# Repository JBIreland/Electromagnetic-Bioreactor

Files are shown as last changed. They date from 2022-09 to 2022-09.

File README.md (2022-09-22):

# Electromagnetic-Bioreactor

The electromagnet enclosure was designed to be a safe and non-invasive method of modulating cellular substrate stiffness to induce biomimetic mechanical stimulation to matured and differentiating cardiomyocytes. This bioreactor is complimentary to the iron nanoparticle infused hydrogels developed in previously published works (1). Each of the electromagnets (APW Company, EM137-24-222) has a holding capacity of 20kg when 24V 0.2Amps is applied. The displacement of nanoparticles within the hydrogels is accomplished by modulation of the electromagnetic fields from 0 to 100% field strength, and the nature of an electronically controlled magnetic system provides precision application of the electromagnetic field. This enables tuning of differences observed in contraction profiles between immature and mature or healthy and diseased cardiomyocytes to be applied to the substrate of cells in culture that could potentially influence preconditioning or chamber specification of differentiating stem cell derived cardiomyocytes.

Physical design of the electromagnetic bioreactor
The layout of the electrical components for this bioreactor are displayed in the attached images. The key components of the system are the Digilent Analog Discovery 2 (Digilent, 410-321) and the OPA541 operational amplifier power module. The Digilent Analog Discovery 2 is a USB controlled oscilloscope, logic analyser, and variable power supply. It can be used straight out the box without modification and is controlled via computer software UI called Waveforms. The OPA541 operational amplifier power module is a commercial plastic control board (PCB) that can be purchased from several vendors including Amazon AU. It is designed to reliably amplify complex audio signals through a two phased amplification with an OPA445 followed by a larger OPA541. This design makes it uniquely capable for our application of amplifying complex contraction profiles but requires modifications to improve its reliability and total gain (modifications described in the attached images). Initially the OPA445 (Digi-Key, OPA445AU-ND) and OPA541 (Digi-Key, OPA541AP-ND) that are provided on the purchased power module are low quality and are replaced with better versions of these components from Texas Instruments. Secondly the gain amplification on the power module board is insufficient so 4 SMD resistors are exchanged for different resistance to control a gain amplification of 2 over the OPA445 and a gain amplification of 5 over the OPA541 which provides a total gain amplification of 10 (2x5). Finally, the incoming voltage to the power module board to drive the electromagnets is close to the operational threshold of the input capacitors. It is therefore wise to increase the capacitors operating voltage from 50V to 63V (Digi-Key, P123408-ND) to accommodate the electrical load. The Digilent Analog Discovery 2 and OPA541 operational amplifier power module components together can produce a customised wavefunction that represents the contraction profile of cardiomyocytes, and the amplification of that signal to drive 6 independent electromagnets. Each of the electromagnets (APW Company, EM137-24-222) has a holding capacity of 20kg when 24V 0.2Amps is applied. The operating temperature of the OPA541 operational amplifier power module can reach temperatures exceeding 100oC and thus required the design of a temperature-controlled air-cooling system (displayed in appendix 6). The air-cooling system uses a negative temperature coefficient (NTC) 10K Ohm thermistor (Jaycar, RN3440) that increases fan speed sequentially as temperature increases. The NTC works at a maximum resistance of 10K Ohms when its temperature is at 25oC and its resistance goes down as it gets hotter. The microcontroller used to operate the thermistor and fan speed is an Arduino mega 2560 Rev3 (Arduino, A000067). This type of microcontroller requires customised control software to be uploaded onto it which was created and uploaded using the Arduino IDE 2.0.0. The Arduino provides a 5V power output and reads the returning voltage on pin A0 over a voltage divider network using the 10K Ohm thermistor and a static 10K Ohm resistor. The equation we use to find the output voltage is described in the equation below 

V_out=  R_2/(R_1+R_2 )   x  V_in

Where V_out is the voltage read on Pin A0 of the Arduino microcontroller, R_2 is the static 10K Ohm resistor, R_1 is the NTC thermistor, and V_in is the 5V output voltage from the Arduino microcontroller that’s passed through the voltage divider network. As the temperature of the NTC thermistor increases its resistance decreases and an increased voltage is returned to the Arduino mega. The fan we are using is a 2 wire 24v brushless DC motor fan (Jaycar, X2542). The Arduino isn’t powerful enough to control the fan speed, so we modulate the amount of voltage the fan receives with a 2N7000 N-Channel field effect transistor (JayCar, ZT2400). The electrical schematic for this system is provided in the attached images.
The electromagnets themselves can exceed temperatures of 42oC which would create a hostile environment for cell culture growth and thus we engineered a water-cooling system for the electromagnets. This works using a water-cooling system designed for a home desktop computer and is modified to incorporate our own design of water flow valve and copper coils used for cooling the 540/550 brush motors of RC boats. The water-cooling systems schematic is shown in the attached images and all parts used in the construction of the electromagnetic bioreactor are listed in the parts list.

Operation of the electromagnetic bioreactor
The operation of the electromagnets is operated via the Waveforms software that controls the Digilent Analog Discovery 2. Upon opening he software we select program 4 with Scope of 2x215, Wavegen of 2x256, logic of 16x16, and pattern of 16x16. Selecting this program allows more of the distributed voltage inside the Digilent Analog Discovery 2 to be supplied to the wavegen function as this is what we will use most heavily. Using the protocol panel on the left of the welcome screen we select scope, wavegen, and supplies. In the supplies tab we set both the positive and negative voltage to 5V which provides the Arduino mega 2560 with 5V and 200 mA. This power supply allows the Arduino to run the thermistor regulated cooling fan next to the OPA541 operational amplifier. On the scope panel we set the base time to 2s/division and set the range for both scope channels to 5V. This provides a scope field from +25 to -25V that’s 20seconds long. Consulting the electromagnetic bioreactor schematic in Appendix 6 you can see channel 1 of the scope is connected to the output wavegen before it enters the OPA541 power module and channel 2 is connected to the output of the OPA541 power module. These settings allow for the visualisation of the wave function both before and after it’s been amplified and helps determine the efficiency of the OPA541 power module. In the wavegen tab we control the wave function that’s been generated by the Digilent Analog Discovery 2 that will be delivered to the electromagnets to manipulate the cells substrate. For testing we used a sine wave with a 1Hz frequency, an amplitude of 2.4V and offset of 0V, a symmetry of 50% and a phase of 0o. These settings are controlled from the “simple” panel in the wavegen tab. By switching to the “custom” panel in the wavegen tab we are presented with a panel with a multitude of options for designing a waveform. By selecting “File” we can upload a file that’s been normalized from 0 to 100% for the contraction profile of cardiomyocytes we have previously measured in the lab. Once the file has been uploaded, the contraction profile is present in the wavegen graph. We now click on run in the wavegen, scope, and supplies tabs and turn on the two bench power supplies supplying the input voltage to the OPA541 power module. We can now see in the scope window that the 2.4V sign wave being produced from the wavegen tab is displaying as two sign waves on the scope tab. The initial wavegen with an amplitude of 2.4V from channel 1 and a second wavegen with an amplitude of 24v from channel 2. We can then save these settings so we don’t need to reconfigure the waveforms software every time we run an experiment and we can run these wavegen programs continuously. 

Reference

1. Islam MS, Molley TG, Ireland J, Kruzic JJ, Kilian KA. Magnetic Nanocomposite Hydrogels for Directing Myofibroblast Activity in Adipose‐Derived Stem Cells. Adv NanoBio Res. 2021 Apr;1(4):2000072.

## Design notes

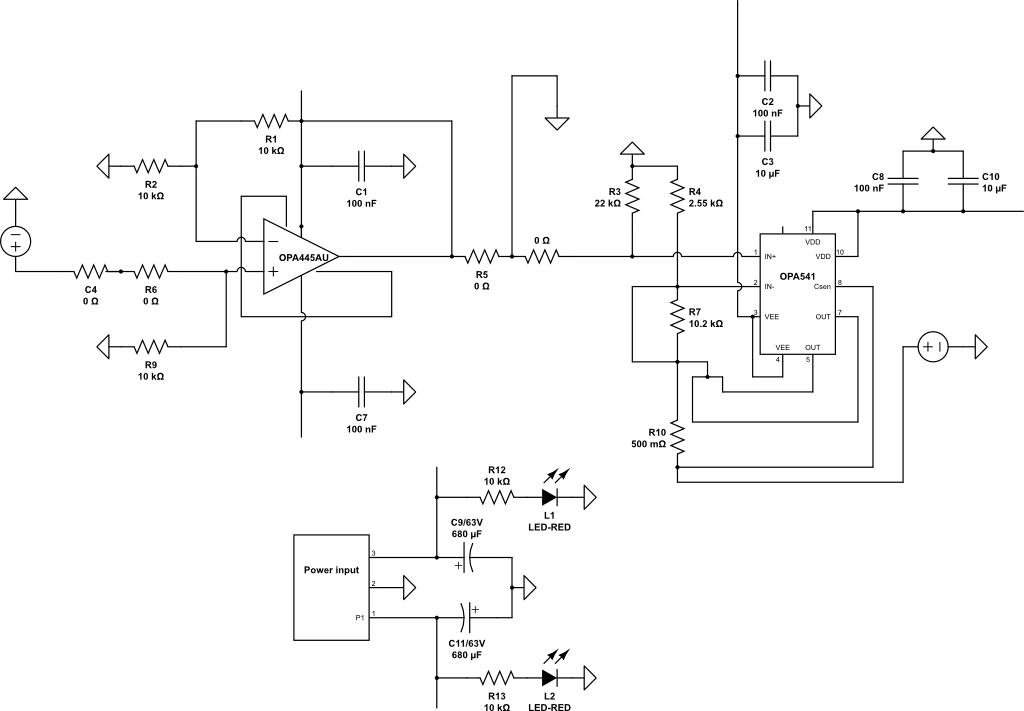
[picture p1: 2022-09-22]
OPA541 modification/OPA541 Power Module modified-schematic.png

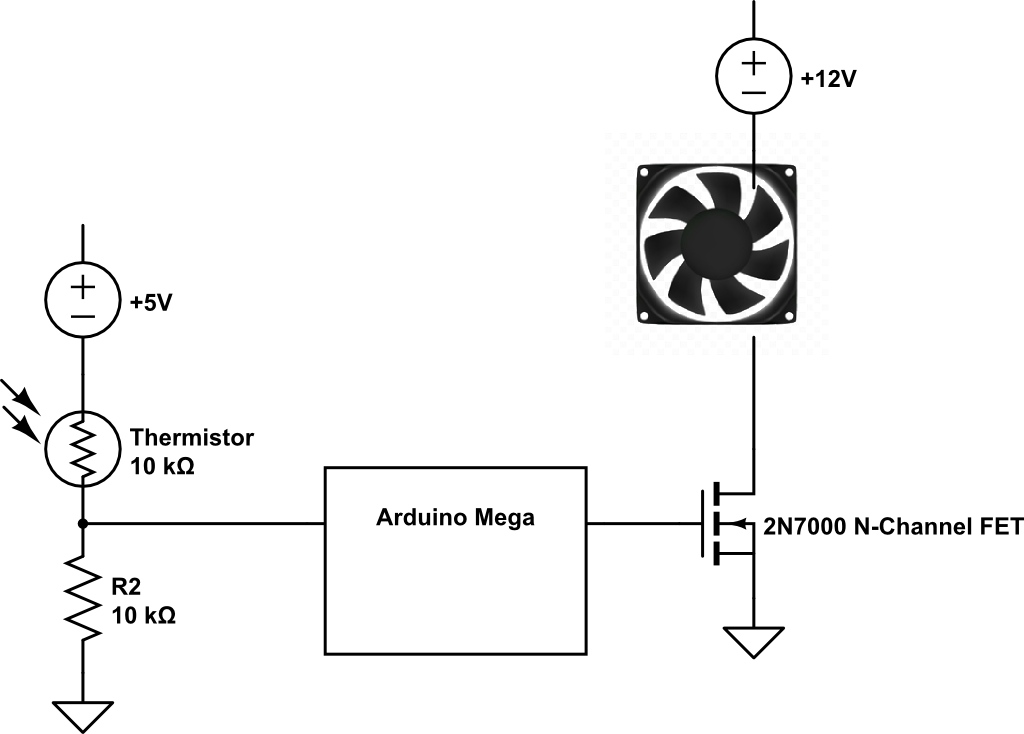
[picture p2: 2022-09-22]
fan_Control/fan-control-thermistor.png

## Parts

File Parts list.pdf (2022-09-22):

Parts list

Quantity | Part | Product Code | Company
6 | Electromagnets | EM137-24-222 | APW Company
| Copper Board | HP9558 | Jaycar
8 | 2 Way PCB Mount Screw Terminals 5mm Pitch | HM3172 | Jaycar
2 | 2 Pole PC Mount Pluggable Header -5.08mm - Vertical | HM3112 | Jaycar
2 | 2 Pole PC Mount Pluggable Header -5.08mm - Horizontal | HM3102 | Jaycar
4 | 2 Pole PC Mount Pluggable Terminal Block Socket - 5.08mm | HM3122 | Jaycar
1x20pack | Crimp Ferrule White 0.75mm² | PT4433 | Jaycar
1x 20pack | Crimp Ferrule Red Terminal Pack | PT4533 | Jaycar
1 pack | Breadboard Jumper wires | PB8850 | Jaycar
1 pack of 40 | 150mm Socket to Socket Jumper Leads | WC6026 | Jaycar
1 pack of 40 | 150mm Plug to Plug Jumper leads | WC6024
1 pack of 40 | 150mm Plug to Socket Jumper Leads | WC6028 | Jaycar
1 | OPA541 Module Power Amplifier Audio Amplifier | | Amazon AU
1 | Operational Amplifier OPA445 | OPA445AU-ND | Digi-Key
1 | Operational Amplifier OPA541 | OPA541AP-ND | Digi-Key
1 | 2.55K OHM SMD Resistor | P2.55KDACT-ND | Digi-Key
1 | 10.2K OHM SMD Resistor | P10.2KDACT-ND | Digi-Key
1 | 10K OHM SMD Resistor | P10KDACT-ND | Digi-Key
2 | 0 OHM SMD Resistor | P0.0KDACT-ND | Digi-Key
1 | 10K Resistor | | Elegoo
2 | Capacitors Cap Alum 68UF 20% 63V THRU HOLE | P123408-ND | Digi-Key
1 | 80mm 24VDC 2 wire Brushless Fan Motor | X2542 | Jaycar
1 | 80mm Plastic Fan Guard | YX2552 | Jaycar
1 | Arduino Mega 2560 Rev3 | A000067 | Arduino

1 | 10kΩ Epoxy Dip NTC Thermistor | RN3440 | Jaycar
1 | 2N7000 N-Channel FET | ZT2400 | Jaycar
1 | Analog Discovery 2: 100MS/s USB Oscilloscope, Logic Analyzer and Variable Power Supply | 410-321 | Digilent
1 roll | Narva 3mm x 10m 10Amp Red/Black Twin core power cable | 0047792 | Bunnings
2 | 30V 10A DC Power Supply | 72-2925 | Element14
1 | 3 Way Red WAGO PUSH WIRE Connector | HM3233 | Jaycar
1 | Breadboard | PB8815 | Jaycar
1 | 24V DC 1.25A Power Supply | MP3494 | Jaycar
1 | 5V DC 3A Slim Power Supply | MP3480 | Jaycar
1 | 12V DC 400mA Ultra-Slim Power Supply | MP3147 | Jaycar
1 | 3-12V DC 27W Power Supply | MP3316 | Jaycar
1 | Plastic Storage Container 10L Rectangular | 881880 | Sistema
1 | 900x600x5mm Clear Acyrlic Sheet | 1010490 | Bunnings
1 | Dark Grey Enclosure with Mounting Flange - 171(W) x 121(D) x 55(H)mm | HB6125 | Jaycar
1 | 3D Printed Bioreactor Cooling Valve | | Printed in house in Polycarbonate
1 | Kinetic O Ring Assorted Kit | 4920305 | Bunnings
1 | Pacific RL120 Radiator | CL-W011-AL00BL-A | Thermaltake
1 | 120mm PWM Curve Fan | CL-W069-CA00BL-A | Thermaltake
1 | Pacific PR22-D5 Plus 300mL Resevouir and D5 pump | CL-W187-PL00SW-A | ThermalTake
1 meter | V-Tubler 4T | CL-W019-OS00TR-A | Thermaltake
2 meters | uxcell Silicone Tubing 3/8 inch(9mm) ID x 1/2 inch(12mm) OD | | Uxcell (Amazon AU)

1 meter | Silicone tubing 4mm ID | | Uxcell (Amazon AU)
2 | 2 Way Ball Valve G1/4 Black | 3831109847305 | EK Waterblocks
2 | Themaltake Pacific 1/2in ID 3/4in OD Compression Fitting Black | CL-W030-CA00BL-A | Thermaltake
8 | Thermaltake Pacific 3/8'' ID x 1/2'' OD Compression - Black | CL-W033-CA00BL-A | Thermaltake
6 | Copper Water cooling Jacket Ring for 540/550 Brush Motor | | Fielect (Amazon AU)
6 | Donut/Pi Disc, Grade A, Copper Plated, Donut Width: 11.5mm, 30x6mm, Hole: 7mm | G-F424-06F | Jewelry And Findings
3 packs | Pinnacle M4 x 35mm Stainless Steel Hex Head Bolts And Nuts | 0130511 | Bunnings
1 pack | Pinnacle M4 Galvanised Coupler | 1101061 | Bunnings
1 | Selleys Silicon Glass 75g Clear | 1230363 | Bunnings

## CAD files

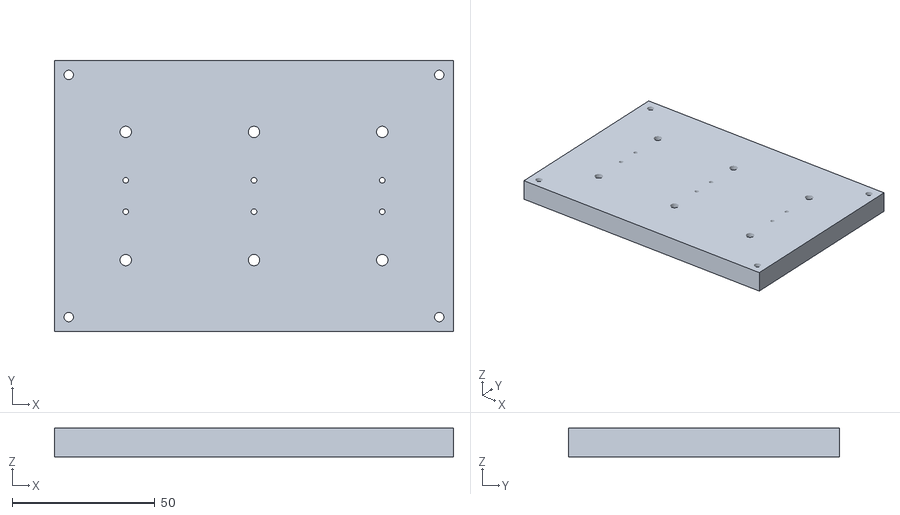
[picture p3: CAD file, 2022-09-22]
3D Printing/Electromagnet Housing Lid.stl
140.0 x 95.0 x 10.00

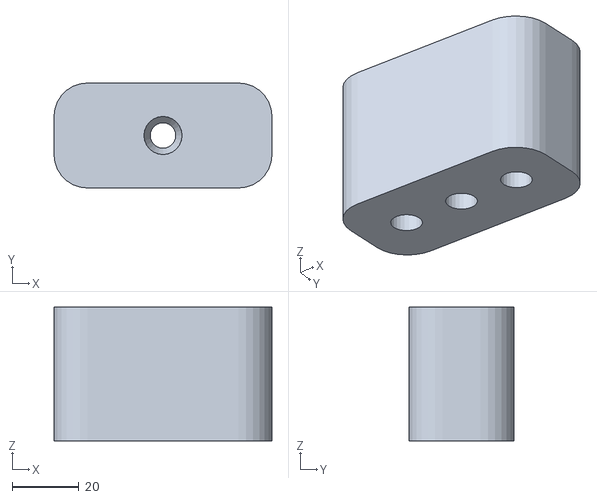
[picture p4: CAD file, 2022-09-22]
3D Printing/Bioreactor cooling valve.stl
65.2 x 31.4 x 40.0

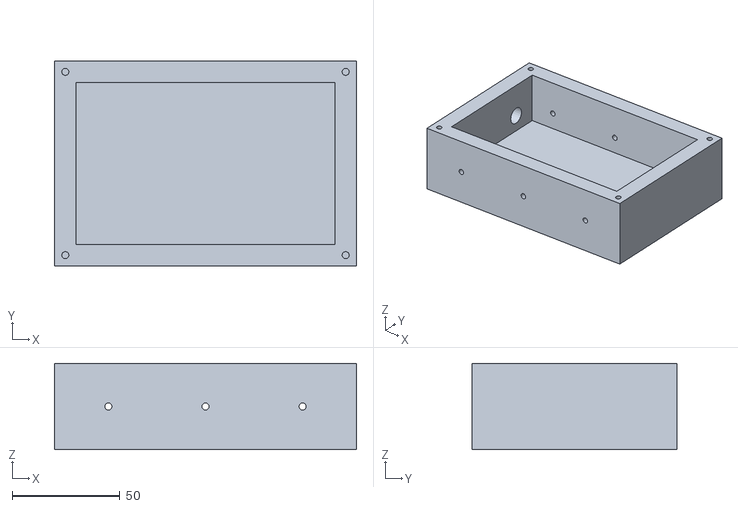
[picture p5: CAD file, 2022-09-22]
3D Printing/Electromagnet Housing .stl
140.0 x 95.0 x 40.0

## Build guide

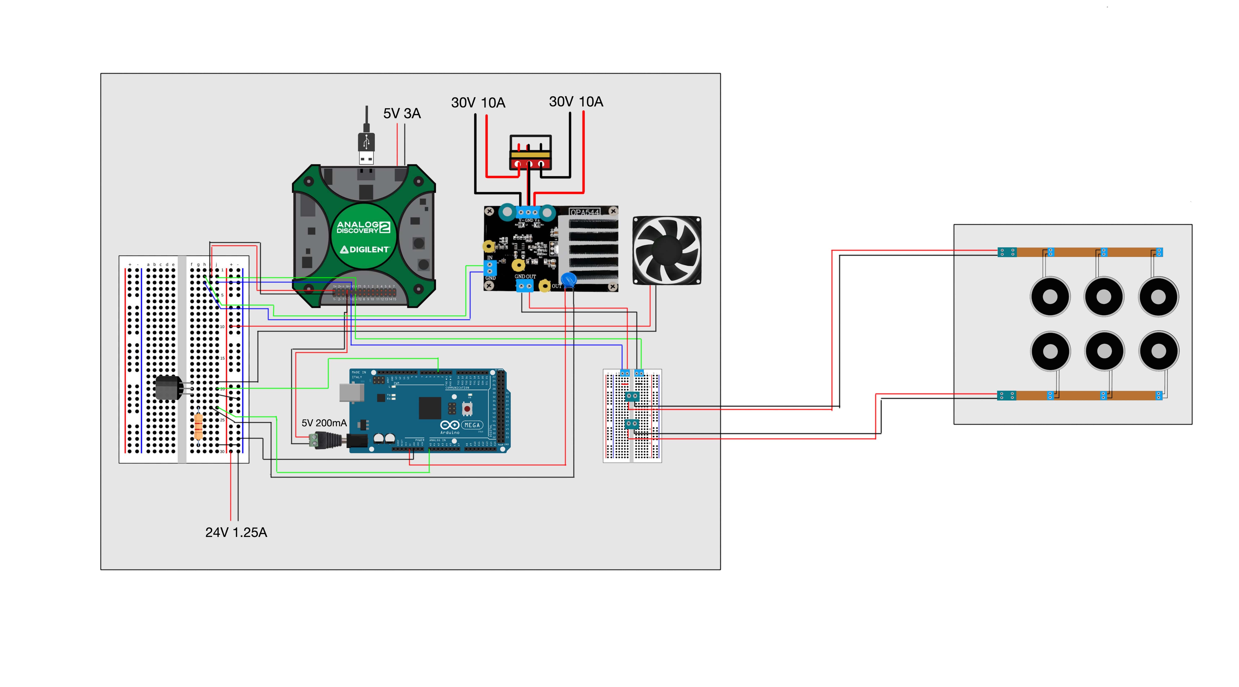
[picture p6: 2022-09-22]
Construction Schematic/Electromagnetic Bioreactor Shematic1.jpg

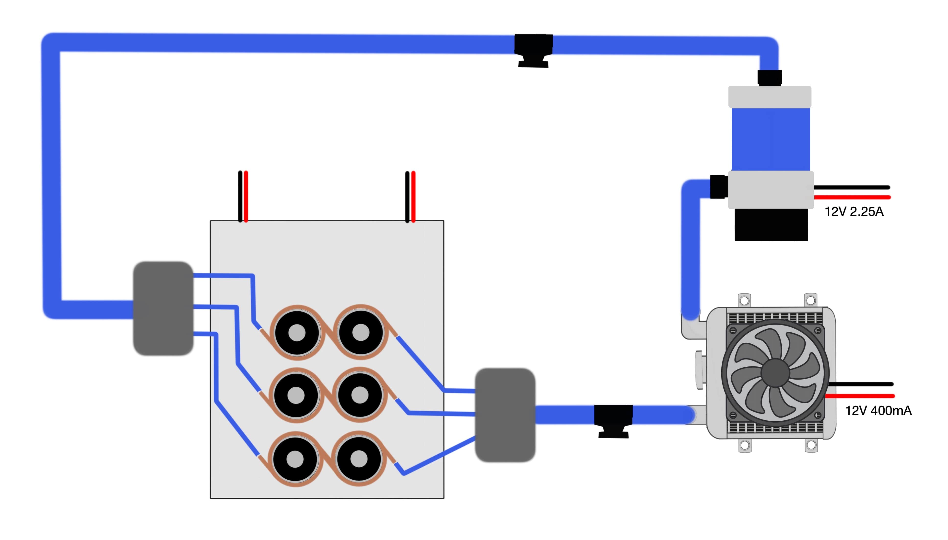
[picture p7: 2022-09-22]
Construction Schematic/Water cooling system2.jpg

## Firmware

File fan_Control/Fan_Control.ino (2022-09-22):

int sensorPin = A0;
int PWM = 3;
int sensorValue;
int PWMValue;

void setup() {
  // put your setup code here, to run once:
  pinMode(sensorPin, INPUT);
  pinMode(PWM, OUTPUT);
  Serial.begin(9600);

}

void loop() {
  // put your main code here, to run repeatedly:
  //this code prints sensor value to the console
  Serial.println(sensorValue);
  delay(1000);

  //read sensor value and set upper limit cap
  sensorVal = analogRead(sensorPin);
  if(sensorValue >800){
    sensorValue = 800;
  }

  //map and assign pwm values to the fan output 0 to 255 corresponds to 0 to 100%
  PWMValue = map(sensorValue, 450, 800, 26, 255);

  //set 450 as out cutout or cut in limit where the fan switches from off to the lower PWM limit
  if(sensorValue <450){
    PWMValue = 0;
  }

  //write the PWM value to the pwm output pin
  analogWrite(PWM, PWMValue);

}
